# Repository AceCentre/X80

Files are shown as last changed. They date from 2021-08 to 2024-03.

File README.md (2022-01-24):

# X80

X80 is an Arduino-based multi-functional input/output device designed to be an interface between assistive technology inputs such as accessibility switches or specilist sensors and mainstream technology outputs, such as to a mobile phone or Augmentative and Alternative Communication (AAC) device.

An X80 can be preprogrammed and repurposed to perform a different function. It's built around the Adafruit Feather, generally the nrf82540 Express. It's essentially a Feather Wing for Assistive Technology (AT).

There are a couple of smilar projects:

https://github.com/google/mimosa

https://github.com/asterics/FABI

The PCB is still a work in progress but it is designed to have:

* Switch inputs via 3.5mm jack
* switch outputs via 3.5mm jack (simulates a switch press as an input into an Assistive Technology device)
* DB9 connector designed to accomodate devices meeting the TRACE SET Standard often used with accessibility input devices (https://park.org/Guests/Trace/pavilion/setdoc1.htm)
* buzzer
* potentiometer
* on/off switch

There are a few differences between the prototype versions:

## Version 4

The funtionality has been split into two boards:

* X80 Standard (designed for Adafruit ItsyBitsy nrf52840 https://www.adafruit.com/product/4481)
* X80 Power (required for LIPO battery as this board includes the chargin circuit)

### X80 Standard

* Majority surface mount components
* 4 switch inputs (5 with splitter cable on one port)
* 4 switch outputs
* One switch 'pass through' (one switch input will still control on switch output without power)
* buzzer
* setting potentiometer
* header for connecting X80 Power or wiring direct to board)

### X80 Power

* JST connector for LIPO battery
* DB9 connector for connecting external peripherals
* will allow space in enclosure for LIPO battery

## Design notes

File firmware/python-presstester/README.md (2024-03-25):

# Python Press Tester

Designed to Have a switch lead in a Switch jack and repeatedly press it once a second

- Its outputting Switch On/Off But I dont think Im actually pressing the switch output correctly 
- Its not changing the dotstar colour. I dont know why

**NB: ITS CIRCUITPYTHON 9. You NEED THE CIRCUITPYTHON 9 Libraries and firmware for this**

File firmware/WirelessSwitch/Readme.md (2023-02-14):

# Wireless Switch

> ! This is historic - Now see https://github.com/AceCentre/OWS for the most up-to-date  details

## What does this do?

You have a nrf52840 board that sends and a nrf52840 board that receives. We are demonstrating here how to do wireless switches with LOW POWER. 

## How?

Most wireless switches either use Radio (e.g. LoRa) or BLE HID to operate. The problem with BLE HID is that its power hungry and for switch users it cant really sleep. So this technique has a advertisement (advertisement) beacon which starts advertisement on a switch press. Full detail below.. 

On the advertisement (switch sending) board:
- When device sleeps and key button pressed first time, board wakes up. Once the LED lights the board is ready and you can start pairing or transmitting button data.
- When switch is pressed again board starts collecting button data into packages and advertise them.
- It then sends out packages. These data packages are changed every 100ms. Each package has recorded 10 buttons states with interval 10 ms(which in total 100ms).
- After some time of inactivity (5sec default) it will go back to sleep.

On the central (dongle) side:
- It scans BLE devices and for the MAC address device it receives package which has recorded button states over 100ms and then replays these states via USB keyboard (of course you could choose to do this as a joystick button or whatever. That I'm not too bothered about)

## Details

To try this out get two [nrf52840 feather express boards](https://www.adafruit.com/product/4062) from adafruit. Then load up the firmware for each board (its a arduino sketch - you want to first follow the guide [here](https://learn.adafruit.com/introducing-the-adafruit-nrf52840-feather/arduino-bsp-setup)). 

The firmware for the switch sending part is called *advertisement*. You need to add two switches -  one for the actual switch (use a switch jack) and a tactile swich for pairing. 

The firmware for the recievfing part is known as the *central* firmware. There should be defined a LED for indicating pairing. By default it's the red led of a nrf52840 Feather express.

When pairing button is pressed on the advertisement board it will send a specific pairing package and dongle receives this package and MAC address of the board it will listen for. The MAC is saved in flash memory and can be read later on start of dongle code.

Note - to save battery the advertisement board is set to sleep. Pressing the switch will wake it up - all in all this takes around 1 second. 

## Software only technique

So you can use a nrf52840 USB dongle to receive the switch press - or right now you could do it in software alone. See the python directory for this code. 

## Battery life estimates

When pressing key buttton and transmitting data, it consumes around 1000 uA.
In sleep mode it consumes 20 uA.
Good coin cell battery can have around 200 mAh.
So 200mAh/20uA = 10000 hrs in deep sleep mode.
10000hrs > 416 days > a bit more than a year.

But in general cheap batteries will have less capacity.

Consumption can also vary on different boads. My measurements were made with nrf52840 dongle.

## Hardware options

Pretty much any nrf52840 that you can load an arduino sketch onto. 
E.g. 

- [SEEED XIA0 nrf52840](https://shop.pimoroni.com/products/seeed-xiao-ble-nrf52840-supports-arduino-micropython-bluetooth5-0-with-onboard-antenna). Super small - will take a lipo if you solder onto the back batt pins
- [Adafruit nrf52840 express](https://shop.pimoroni.com/products/adafruit-feather-nrf52840-express). A great develeopment board. Has a spare button for you to use as either a pairing button or sending button. 
- [Adafruit itsybitsy nrf52840](https://shop.pimoroni.com/products/adafruit-itsybitsy-nrf52840-express-bluetooth-le). Same as the feather - but smaller and slight less flashy

And for the dongle
- This is nice as its all in one piece. [nrf52840 USB key](https://thepihut.com/products/nrf52840-usb-key-with-tinyuf2-bootloader-bluetooth-low-energy-mdbt50q-rx)

## Roadmap

- [x] Get basic code working
- [x] Add in pairing functionality
- [ ] Get video demo working
- [x] Add in low power features
- [ ] Adapt for x80 
- [x] Write demo code for PC (1/2 done. Can receive switches not send)
- [ ] Create docs page on Ace site
- [ ] Add ability to listen for more than one switch

## Licence

MIT

## Credits 

Will Wade, With a big nod to Prente Romiche/Saltillo and their aeroswitch. Note  - I have no idea if there's does exactly the same as this but a big clue was the fact they called it "Broadcast mode"

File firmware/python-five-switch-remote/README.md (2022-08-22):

# Five Switch Remote

This firmware is a CircuitPython based remote control with five switches.

The centre switch should be plugged into the switch port marked '0' on the X80. The other switches should be plugged into the other jacks and (with a splitter in the port marked '3+').

The four direction arrows will map to a keypress on the coresponding arrow key. You can click and hold for a longer keypress, the press is passed directly through.

The centre key has three options:

- Short press - Will press space
- Medium press - Will press CMD+H
- Long press - Will press EJECT followed by CTRL+TAB

The timings and keys can all be configured in the `user_constants.py` file.

The x80 will pulse with a blue light when it is in 'pairing' mode.

## Setting up circuit python

1. [Download the CircuitPython firmware for the X80 here](https://circuitpython.org/board/itsybitsy_nrf52840_express)
2. [Follow the instructions to flash Circuit Python firmware to the device here](https://learn.adafruit.com/adafruit-itsybitsy-nrf52840-express/circuitpython)
3. Drag the contents of this folder (`python-switcher`) onto the CIRCUITPY device.
4. Done!

To develop the code use [`Code With Mu`](https://codewith.mu/). It will automatically connect to the device if its plugged in. You can set it up with VSCode but honestly its not worth the hassle

## Configuration

All of the X80 configuration is found in `x80_constants.py`. This creates a bunch of constants specific to the x80 like what switches are connected to what pins and what pull mode the switches are in. These shouldn't need to be changed between users.

The `user_constants.py` is where we can tweak the behaviour of the switcher. Change which ports we want to enable and the colors of the LED etc.=xnk

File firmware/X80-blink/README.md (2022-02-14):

# X80-blink
Demonstrate blink detection using the X80 interface device.

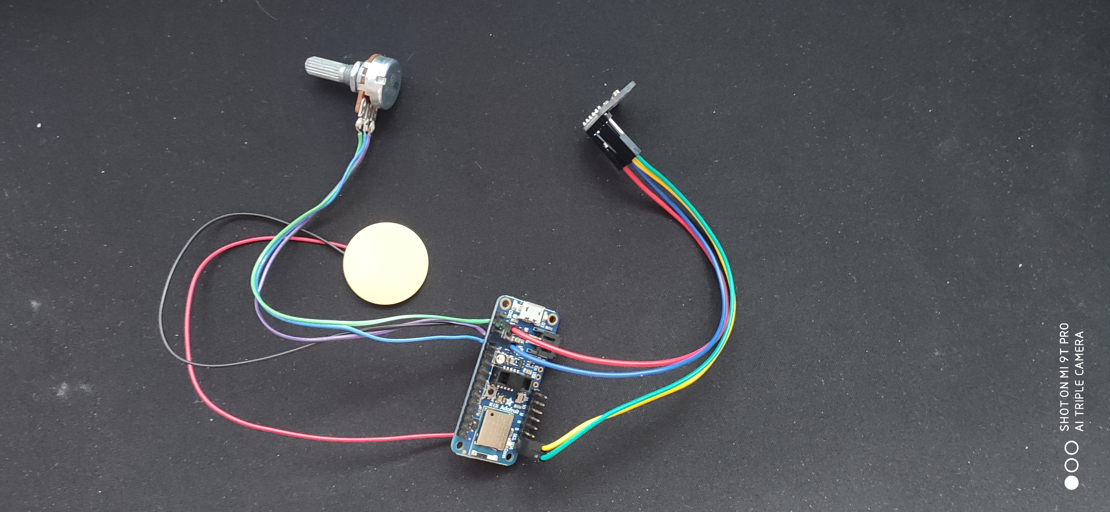
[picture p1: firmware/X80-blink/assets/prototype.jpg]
Breadboard prototype


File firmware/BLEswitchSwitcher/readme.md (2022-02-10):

What does this do?

- Use one or two switches
- Pair it with your device
- With switch 3 - it will change the MAC address of the device
- With switch 4 - It will change the name of the device

This theoretically means you can use one switch for different apps on Android - or on iOS swap the mac address

** WARNING: NOT TESTED **

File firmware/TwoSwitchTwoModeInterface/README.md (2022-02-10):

# TwoSwitchTwoModeInterface
 Simple Arduino/Adafruit nrf52840 express feather sketch demonstrating how to change MAC address

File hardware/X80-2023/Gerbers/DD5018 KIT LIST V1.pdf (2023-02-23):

Assembly Ref | A06-02 | Job No. | C2698 | Kit Prep 1 hour | Assembly time ?? mins per board
Build Qty | 1 | UNIT WEIGHT
Mj Ref | Qty per board | Kit Qty | Kitted | Board Ref | Description | Suppler | Ref
A06-01 | 1 | 1 | 1 | A1 | ADAFRUIT FEATHER BASIC ATSAMD21 CORTEX M0 | MOUSER | 485-2772
A06-02 | 1 | 1 | 1 | BUZ1 | AUDIO MAGNETIC XDCR 3-5V SMD | Digikey | 102-3736-1-ND
A06-03 | 10 | 10 | 20 | C1, C2, C3, C4, C5, C6, C7, C8, C10, C11 | CAP CER 10NF 50V X7R 0603 | Farnell | 2346966
A06-04 | 2 | 2 | 5 | D1, D2 | DIODE GEN PURP 100V 300MA SOD123 | Farnell | 3127171
A06-05 | 0 | 0 | 9 | J1, J2, J4, J6, J7, J8, J9, J10, J11 | 3.5 mm PCB Mount Stereo Jack Socket, 4Pole 1A | Farnell | 2677783
A06-06 | 1 | 1 | 1 | J5 | 4 Pole Side Entry Shrouded Header 2.00mm | Rapid | 22-5204
A06-07 | 1 | 1 | 1 | K1 | DPDT telecom PCB relay, 2A 3Vdc coil, EA | Farnell | 1326155
A06-08 | 2 | 2 | 5 | Q1, Q2 | TRANS NPN 40V 0.6A SMD SOT23-3 | Farnell | 1773626
A06-09 | 1 | 1 | 5 | Q3 | BIASED 50V 100mA | Farnell | 3368898
A06-10 | 1 | 1 | 10 | R1 | RES SMD 3.3K OHM 1% 1/10W 0603 | Farnell | 9238549
A06-11 | 2 | 2 | 10 | R2, R7 | RES 1K OHM 0.1% 1/10W 0603 | Farnell | 2502396
A06-12 | 1 | 1 | 10 | R3 | RES SMD 100K OHM 1% 1/10W 0603 | Farnell | 9238727
A06-13 | 1 | 1 | 5 | R4 | 10kΩ, Trimmer Potentiometer 0.2W Top Bourns, 3306P | Farnell | 108239
A06-14 | 2 | 2 | 10 | R5, R6 | RES SMD 4.7K OHM 5% 1/10W 0603 | Farnell | 9233466
A06-15 | 11 | 11 | 20 | R8, R9, R10, R11, R12, R18, R19, R20, R21, R22, R23 | RES SMD 100 OHM 1% 1/10W 0603 | Farnell | 9238360
A06-16 | 4 | 4 | 10 | R13, R14, R15, R16 | RES SMD 390 OHM 5% 1/10W 0603 | Farnell | 9233326
A06-17 | 1 | 1 | 10 | R17 | RES SMD 22K OHM 5% 1/10W 0603 | Farnell | 9233547
A06-18 | 1 | 1 | 10 | SW1 | PUSHBUTTON SMD | Farnell | 9471898
A06-19 | 4 | 4 | 4 | U1, U2, U3, U4 | 1 Form A Solid-State Relay (NO) | Farnell | 1470184

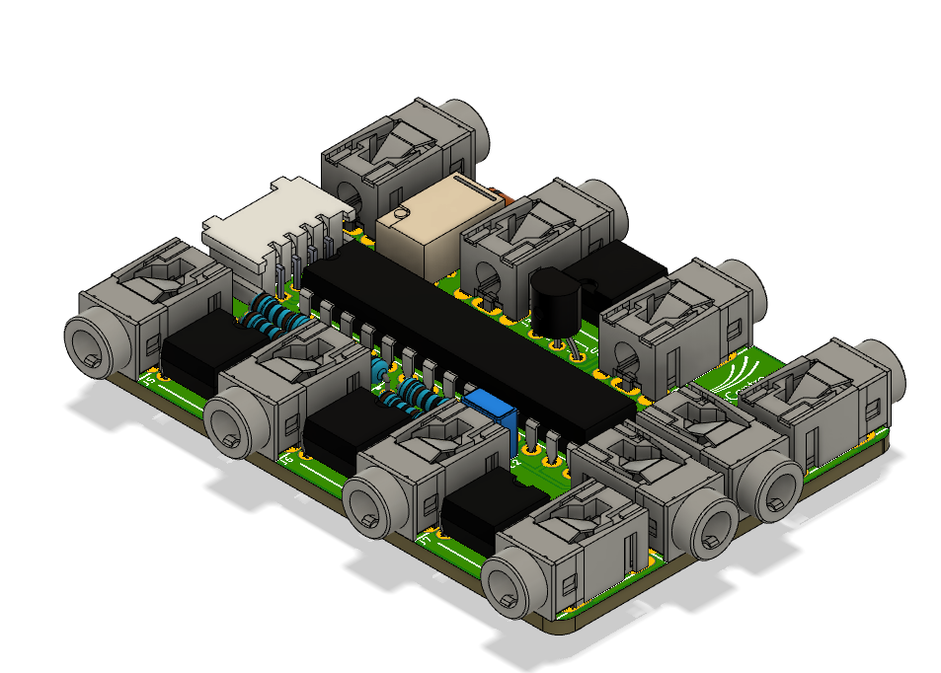
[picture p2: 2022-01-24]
hardware/X80 Wio Terminal/X80 Wio Terminal.png

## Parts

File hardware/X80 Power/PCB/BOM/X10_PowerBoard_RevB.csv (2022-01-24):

Qty | Value | Device | Package | Parts | Description | DESCRIPTION | MF | MFR | MFR_NUM | MPN | OC_FARNELL | POPULARITY | SPICEPREFIX | VALUE | VENDOR | VENDOR_NUM
3 |  | 1,6/0,8 | 1,6/0,8 | PAD1, PAD2, PAD3 | THROUGH-HOLE PAD |  |  |  |  |  |  | 15
1 |  | LEDSML0603 | SML0603 | LED1 | LED |  |  |  |  |  |  | 17
1 | 0.1uF | C-EUC0603 | C0603 | C1 | CAPACITOR, European symbol |  |  |  |  |  |  | 73 | C
1 | 100k | R-100K-1%-0603 | RESC1608X60 | R10 | SMD Resistor | RES SMD 100K OHM 1% 1/10W 0603 |  | Yageo | RC0603FR-07100KL |  |  |  |  | 100k | Digi-Key | 311-100KHRCT-ND
1 | 239-5849 | DB9_MALE-SLOTS | DB9_PLUG_SLOT | J1 | D-SUB Connector - Right Angle | D-sub Connector - 2.77mm Pitch |  | RS Pro | 239-5849 |  |  |  |  | 239-5849 | RS-Online | 239-5849
2 | 4.7uF | C-4.7UF-10V-X5R-0603 | CAPC1608X85 | C11, C14 |  | CAP CER 4.7UF 10V X5R 0603 |  | Samsung Electro-Mechanics | CL10A475KP8NNNC |  | unknown |  |  | 4.7uF | Digi-Key | 1276-1044-1-ND
1 | 470R | R-BACKUP-470R-1%-0603 | RESC1608X60 | R1 | SMD Resistor | RES SMD 470 OHM 1% 1/10W 0603 |  | Yageo | RC0603FR-07470RL |  |  |  |  | 470R | Digi-Key | 311-470HRCT-ND
1 | 5.1k | R-5.1K-1%-0603 | RESC1608X60 | R8 | SMD Resistor | RES SMD 5.1K OHM 1% 1/10W 0603 |  | Yageo | RC0603FR-075K1L |  |  |  |  | 5.1k | Digi-Key | 311-5.10KHRCT-ND
1 | CONN2_05-HEADER | CONN2_05-HEADER | 2X5_HEADER | J3
1 | CONN_02-S2B-PH | CONN_02-S2B-PH | S2B-PH-RA | J4
1 | DMP2035U-7 | P-MOSFET-DMP2035U-7-SOT323 | SOT95P230X110-3N | Q1 | P MOSFET | MOSFET P-CH 20V 3.6A SOT-23 |  | Diodes Incorporated | DMP2035U-7 |  |  |  |  | DMP2035U-7 | Digi-Key | DMP2035U-7DICT-ND
1 | FUSE0603 | FUSE0603 | FUSC1607X75N | F1
1 | LOGO-10MM | LOGO-10MM | LOGO_10MM | U$2
1 | MBR120VLSFT3G | DIODE-SCHOTTKY-20V-1ASOD-123FL | SODFL3616X98N | D3 | Schottky Diode | Semiconductor DIODE SCHOTTKY 20V 1A SOD123FL |  | On Semiconductor | MBR120VLSFT3G |  |  |  |  | MBR120VLSFT3G | Digi-Key | MBR120VLSFT3GOSCT-ND
1 | MCP23008/P | MCP23008/P | DIL18 | U2 | MCP23008
1 | MCP73831 | MCP73831 | SOT23-5P95_270X145L35X35N | U3 | MCP73831 - Single-Cell, Fully Integrated Li-Ion,Li-Polymer Charge Management Controllers | Single-Cell, Fully Integrated Li-Ion,Li-Polymer Charge Management Controllers |  | Microchip | MCP73831T-2ACI/OT |  | unknown |  |  | MCP73831 | DigiKey | MCP73831T-2ACI/OTCT-ND
1 | SDPT | SLIDE_SWITCH | OS102011MA1QN1 | S2 | Switch Slide Right Angle SPDT 0.1A 12VDC Through Hole Slide Switch SPDT On-On 0.1 A@ 12 V dc Slide | Switch Slide Right Angle SPDT 0.1A 12VDC Through Hole Slide Switch SPDT On-On 0.1 A@ 12 V dc Slide |  | C & K COMPONENTS | OS102011MA1QN1 |  |  |  |  | SDPT | RS-ONLINE
1 | X10_PWR_PCB-X10_PWR_PCB | X10_PWR_PCB-X10_PWR_PCB | X10_POWER_PCB | PCB1

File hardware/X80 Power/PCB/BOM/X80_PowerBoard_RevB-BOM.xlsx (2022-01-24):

Item # | Ref Des | Qty | Description | Manufacturer | Manufacturer part-name | Value | Package
1 | C1 | 1 | CAP CER 0.1UF 25V X7R 0603 | KEMET | C0603C104K3RAC7411 | 0.1uF | 0603
2 | C2, C3 | 2 | CAP CER 4.7UF 10V X5R 0603 | Samsung Electro-Mechanics | CL10A475KP8NNNC | 4.7uF | 0603
3 | D1 | 1 | Semiconductor DIODE SCHOTTKY 20V 1A SOD123FL | On Semiconductor | MBR120VLSFT3G | MBR120VLSFT3G | SOD-123FL
4 | F1 | 1 | PTC RESET FUSE 6V 500MA 0603 | Bourns | MF-FSMF050X-2 | FUSE0603 | 0603
5 | IC1 | 1 | IC I/O EXPANDER I2C 8B 18DIP | Microchip Technology | MCP23008-E/P | MCP23008/P | DIP-18
6 | J1 | 1 | D-sub Connector - 2.77mm Pitch | RS Pro | 239-5849 | 239-5849 | THT
7 | J2 | 1 | CONN HEADER R/A 2POS 2MM | JST Sales America Inc. | S2B-PH-K-S(LF)(SN) | CONN_02-S2B-PH | THT
10 | J3 | 1 | CONN HEADER VERT 10POS 2.54MM | Adam Tech | PH2-10-UA | CONN2_05-HEADER | THT
11 | LED1 | 1 | LED RED DIFFUSED 0603 SMD | Würth Elektronik | 150060SS55040 | RED | 0603
12 | Q1 | 1 | MOSFET P-CH 20V 3.6A SOT-23 | Diodes Incorporated | DMP2035U-7 | DMP2035U-7 | 0603
13 | R1 | 1 | RES SMD 470 OHM 1% 1/10W 0603 | Yageo | RC0603FR-07470RL | 470R | 0603
14 | R2 | 1 | RES SMD 5.1K OHM 1% 1/10W 0603 | Yageo | RC0603FR-075K1L | 5.1k | 0603
15 | R3 | 1 | RES SMD 100K OHM 1% 1/10W 0603 | Yageo | RC0603FR-07100KL | 100k | THT
16 | S1 | 1 | Switch Slide Right Angle SPDT 0.1A 12VDC Through Hole Slide Switch SPDT On-On 0.1 A@ 12 V dc Slide | C & K COMPONENTS | OS102011MA1QN1 | SDPT | 0603
17 | U1 | 1 | Single-Cell, Fully Integrated Li-Ion,Li-Polymer Charge Management Controllers | Microchip | MCP73831T-2ACI/OT | MCP73831 | 0603

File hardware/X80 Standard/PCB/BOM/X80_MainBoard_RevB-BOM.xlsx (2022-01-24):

Item # | Ref Des | Qty | Description | Manufacturer | Manufacturer part-name | Value | Package
1 | BUZ1 | 1 | AUDIO MAGNETIC XDCR 3-5V SMD | CUI Devices | CMT-8530S-SMT-TR | CMT-8530S-SMT | SMD-4
2 | C1, C2, C3, C4, C5 | 5 | CAP CER 10NF 50V X7R 0603 | Samsung | CL10B103KB8WPJC | 10nF | THT
3 | D1, D2 | 2 | DIODE GEN PURP 100V 300MA SOD123 | Diodes Incorporated | 1N4148WQ-7-F | 1N4148 | SOD-123
4 | J1, J2, J3, J4, J8, J9, J10, J11 | 8 | 3.5 mm PCB Mount Stereo Jack Socket, 4Pole 1A | Lumberg | 1503 19 | Stereo Jack | THT
5 | J5 | 1 | CONN HDR 10POS(2x5) 2.54MM GOLD FEMALE THT | Würth Elektronik | 61301021821 | 2x5 | THT
6 | J6, J7 | 2 | CONN HEADER VERT 14POS 2.54MM | Adam Tech | PH1-14-UA | 1x14 | THT
7 | K1 | 1 | DPDT telecom PCB relay, 2A 3Vdc coil, EA | TE Connectivity | 1462037-4 | IM01TS | THT
10 | Q1, Q2 | 2 | TRANS NPN 40V 0.6A SMD SOT23-3 | Diodes Incorporated | MMBT2222A-7-F | MMBT2222A-7-F | SOT-23
11 | R1 | 1 | RES SMD 3.3K OHM 1% 1/10W 0603 | Yageo | RC0603FR-073K3L | 3.3k | 0603
12 | R12, R13, R14, R15, R16 | 5 | RES SMD 100 OHM 1% 1/10W 0603 | Yageo | RC0603FR-07100RL | 100R | 0603
13 | R2 | 1 | RES SMD 100K OHM 1% 1/10W 0603 | Yageo | RC0603FR-07100KL | 100k | 0603
14 | R3, R4 | 2 | RES 1K OHM 0.1% 1/10W 0603 | Yageo | RC0603FR-071KL | 1k | 0603
15 | R5 | 1 | 10kΩ, Trimmer Potentiometer 0.2W Top Bourns, 3306P | Bourns | 3306P-1-103 | 10k | THT
16 | R6, R7 | 2 | RES SMD 4.7K OHM 5% 1/10W 0603 | Yageo | RC0603JR-074K7L | 4.7k | 0603
17 | R8, R9, R10, R11 | 4 | RES SMD 390 OHM 5% 1/10W 0603 | Yageo | RC0603JR-07390RL | 390R | 0603
18 | SW1 | 1 | White Tactile Switch, Single Pole Single Throw (SPST) | Wurth Elektronik | 431256031716 | 431256031716 | THT
19 | U1, U2, U3, U4 | 4 | 1 Form A Solid-State Relay (NO) | Vishay | LH1500AT | LH1500AT | PDIP-6

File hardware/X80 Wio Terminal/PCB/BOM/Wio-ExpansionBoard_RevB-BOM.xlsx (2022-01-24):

Item # | Ref Des | Qty | Description | Manufacturer | Manufacturer part-name | Value | Package | RS-ONLINE_NUM
1 | C1, C2, C3, C4, C5, C6, C7, C8 | 8 | 10nF Multilayer Ceramic Capacitor MLCC 50V dc ±10% | KEMET | C315C103K5R5TA | 10nF | THT | 538-1196
2 | C9 | 1 | Murata 100nF Multilayer Ceramic Capacitor MLCC 50V dc ±15% | Murata | RCER71H104K0K1H03B | 100nF | THT | 841-0749
3 | D1 | 1 | Switching Diode, 400mA 100V, 2-Pin DO-35 1N4148TR | On Semiconductor | 1N4148TR | 1N4148 | THT | 671-5477
4 | J1, J2, J3, J4, J5, J6, J7, J8, J9, J10 | 10 | 3.5 mm PCB Mount Stereo Jack Socket, 4Pole 1A | Lumberg | 1503 19 | Stereo Jack | THT | 124-8885
5 | J11 | 1 | Groove Female Header - DIP-4P-2,0mm-90D |  |  |  | THT | https://www.seeedstudio.com/Grove-Universal-4-pin-connector-90-10-PCs.html
6 | K1 | 1 | DPDT telecom PCB relay, 2A 3Vdc coil, EA | TE Connectivity | 1462037-4 | IM01TS | THT | 909-7996
7 | Q1 | 1 | NPN General-Purpose Amplifier | On Semiconductor | PN2222ABU | PN2222A | TO-92 | 739-0555
8 | R1 | 1 | RS PRO 1kΩ Carbon Film Resistor 0.25W ±5% | RS PRO | 707-7666 | 1k | THT | 707-7666
9 | R2, R3, R4, R5 | 4 | RS PRO 390Ω Carbon Film Resistor 0.25W ±5% | RS PRO | 707-7634 | 390R | THT | 707-7634
10 | U1, U2, U3, U4 | 4 | 1 Form A Solid-State Relay (NO) | Vishay | LH1500AT | LH1500AT | PDIP-6 | 180-8794
11 | U5 | 1 | IC I/O EXPANDER I2C 16-Bit 28SDIP | Microchip | MCP23017-E/SP | MCP23017 | PDIP28 | 144-5723

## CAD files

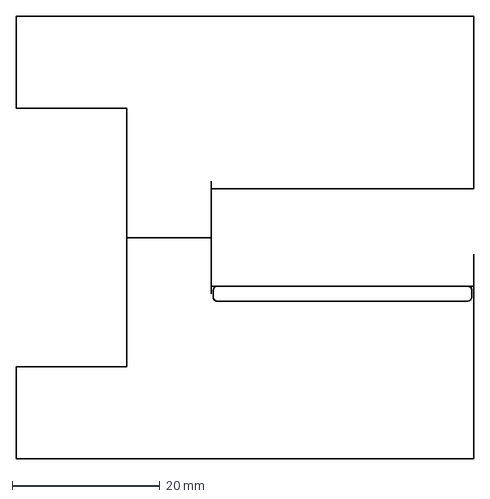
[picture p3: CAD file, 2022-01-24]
hardware/X80 Standard/PCB/Mechanical/MainBoard.dxf
62.0 x 60.0 mm

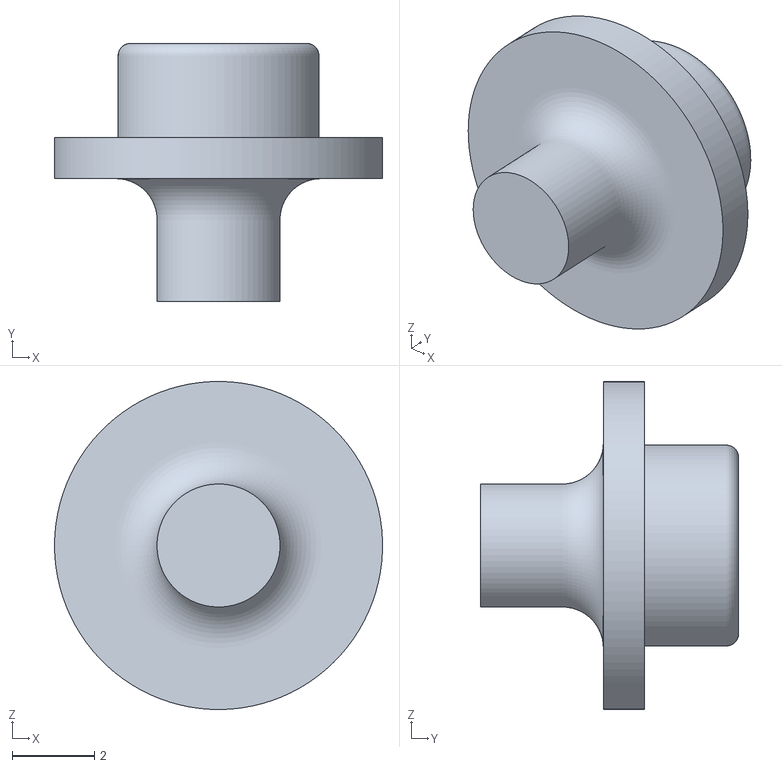
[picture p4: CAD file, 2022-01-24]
hardware/Parts/Lens/630-005-A X80 LED Lens.stl
8.00 x 6.30 x 8.00

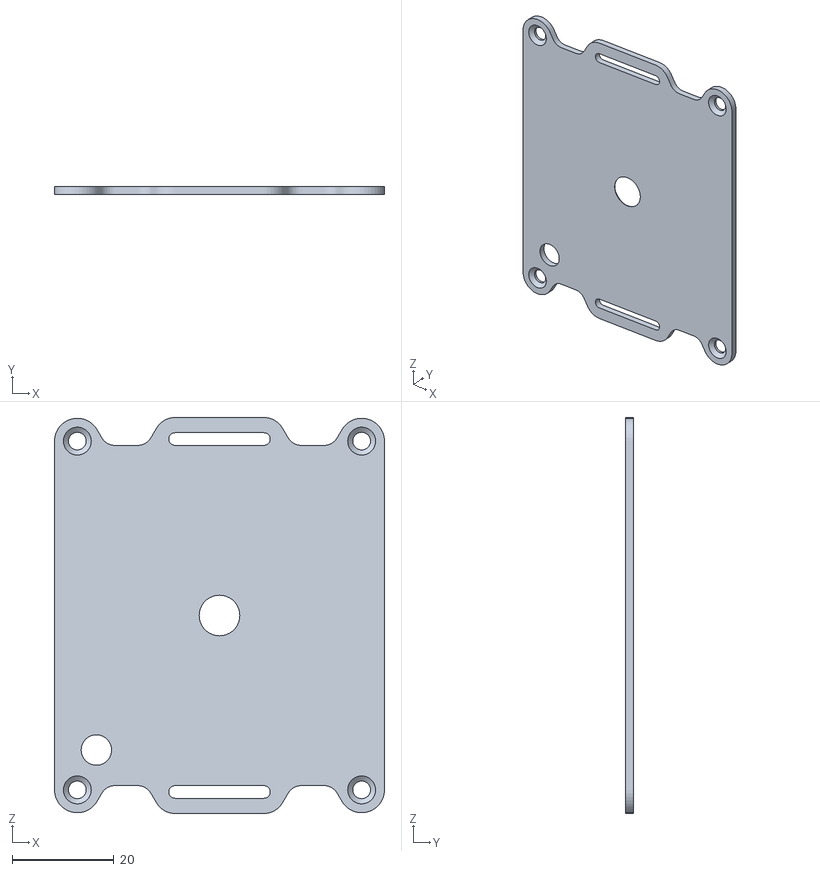
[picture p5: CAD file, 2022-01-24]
hardware/Parts/Mounting Plate/630-006-B X80 Mounting Plate.stl
65.0 x 1.60 x 78.0

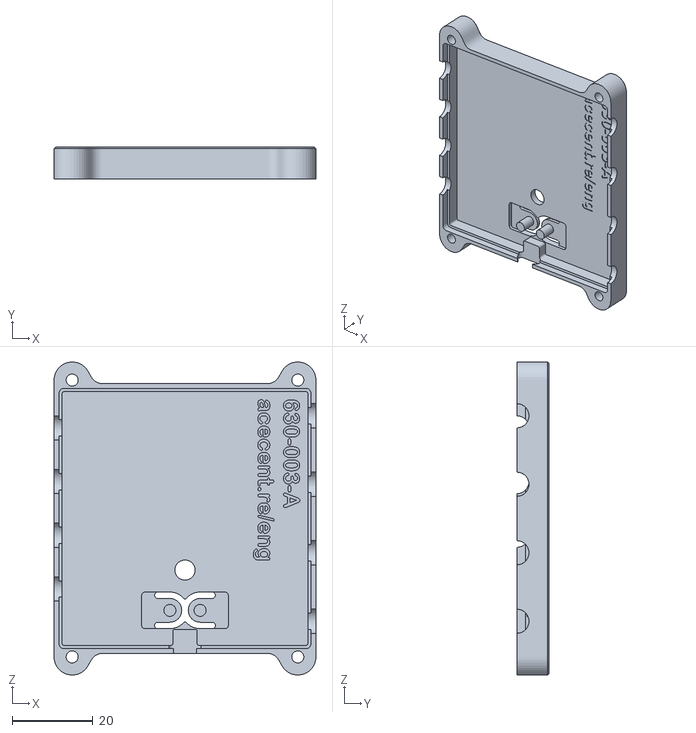
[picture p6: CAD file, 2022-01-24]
hardware/X80 Standard/Enclosure Basic/630-003-A X80 Enclosure Lid Basic.stl
65.0 x 8.00 x 77.7

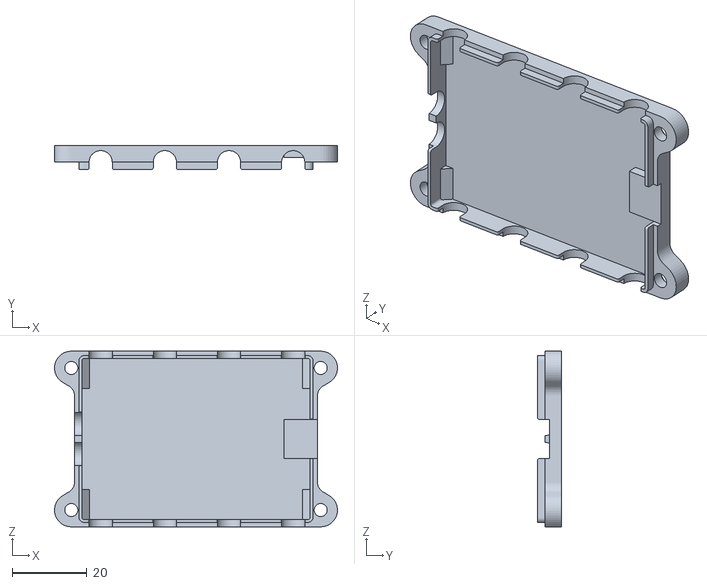
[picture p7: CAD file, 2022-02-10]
hardware/X80 Wio Terminal/Enclosure/630-014 X80 Enclosure Wio Terminal Lid.stl
75.7 x 6.50 x 47.0

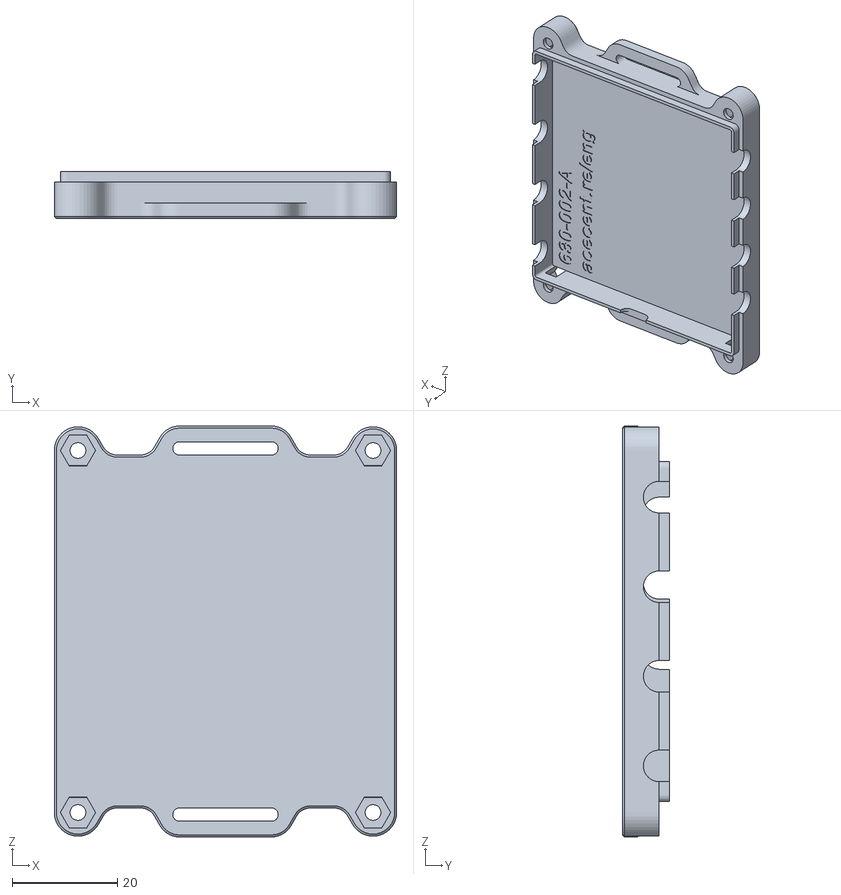
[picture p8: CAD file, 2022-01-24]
hardware/X80 Standard/Enclosure Basic/630-002-A X80 Enclosure Base Basic.stl
65.0 x 9.00 x 78.0

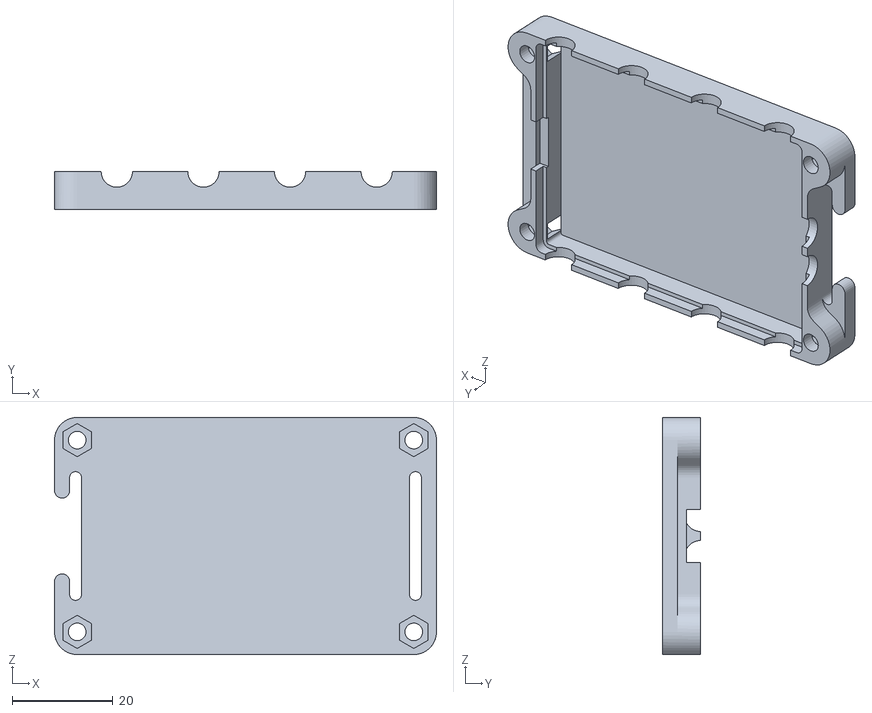
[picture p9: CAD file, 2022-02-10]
hardware/X80 Wio Terminal/Enclosure/630-014 X80 Enclosure Wio Terminal Base.stl
75.7 x 7.50 x 47.0

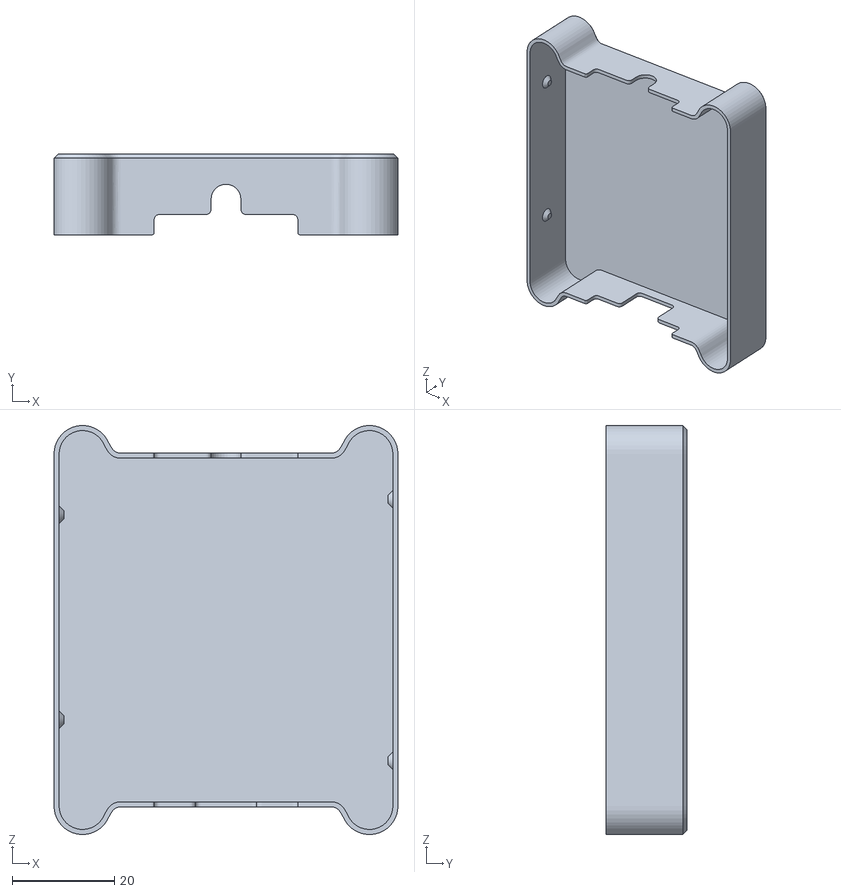
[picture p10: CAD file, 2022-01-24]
hardware/X80 Standard/Enclosure with Grommet/630-011-A X80 Grommet Splash Cover.stl
67.1 x 15.8 x 79.8

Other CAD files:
hardware/X80 Standard/Enclosure with Grommet/630-010-B X80 Enclosure Grommet Lid.stl
hardware/X80 Standard/Enclosure with Grommet/630-009-A X80 Enclosure Grommet Base.stl
hardware/Parts/Mounting Plate/630-006-B X80 Mounting Plate.dxf

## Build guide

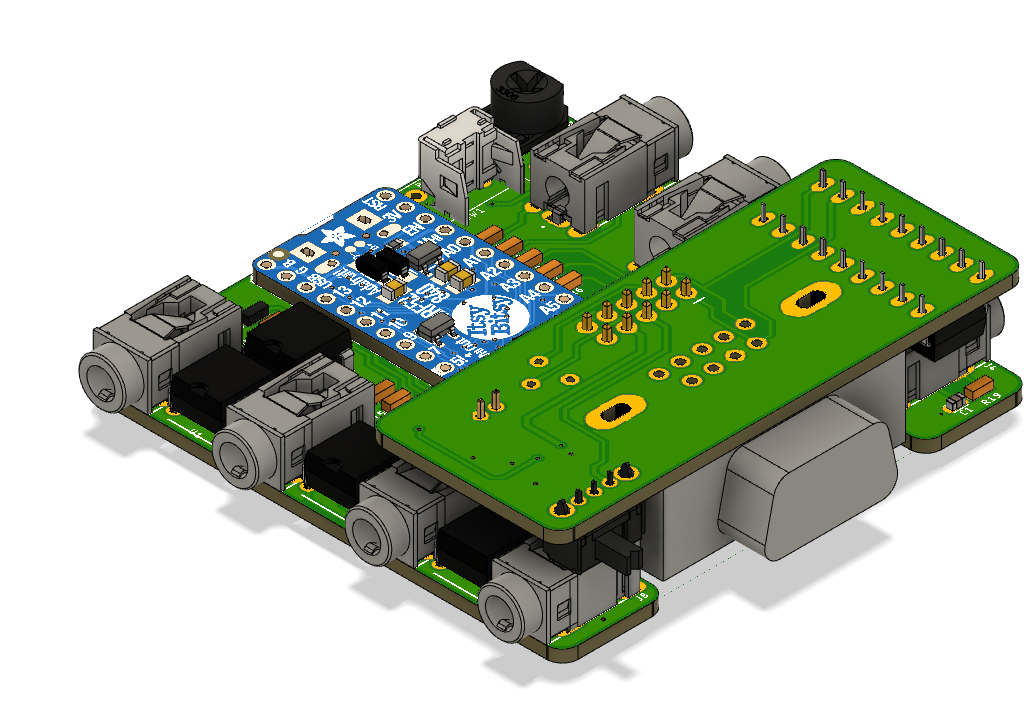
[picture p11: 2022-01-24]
hardware/X80 Power/X80 Power Assembly.png

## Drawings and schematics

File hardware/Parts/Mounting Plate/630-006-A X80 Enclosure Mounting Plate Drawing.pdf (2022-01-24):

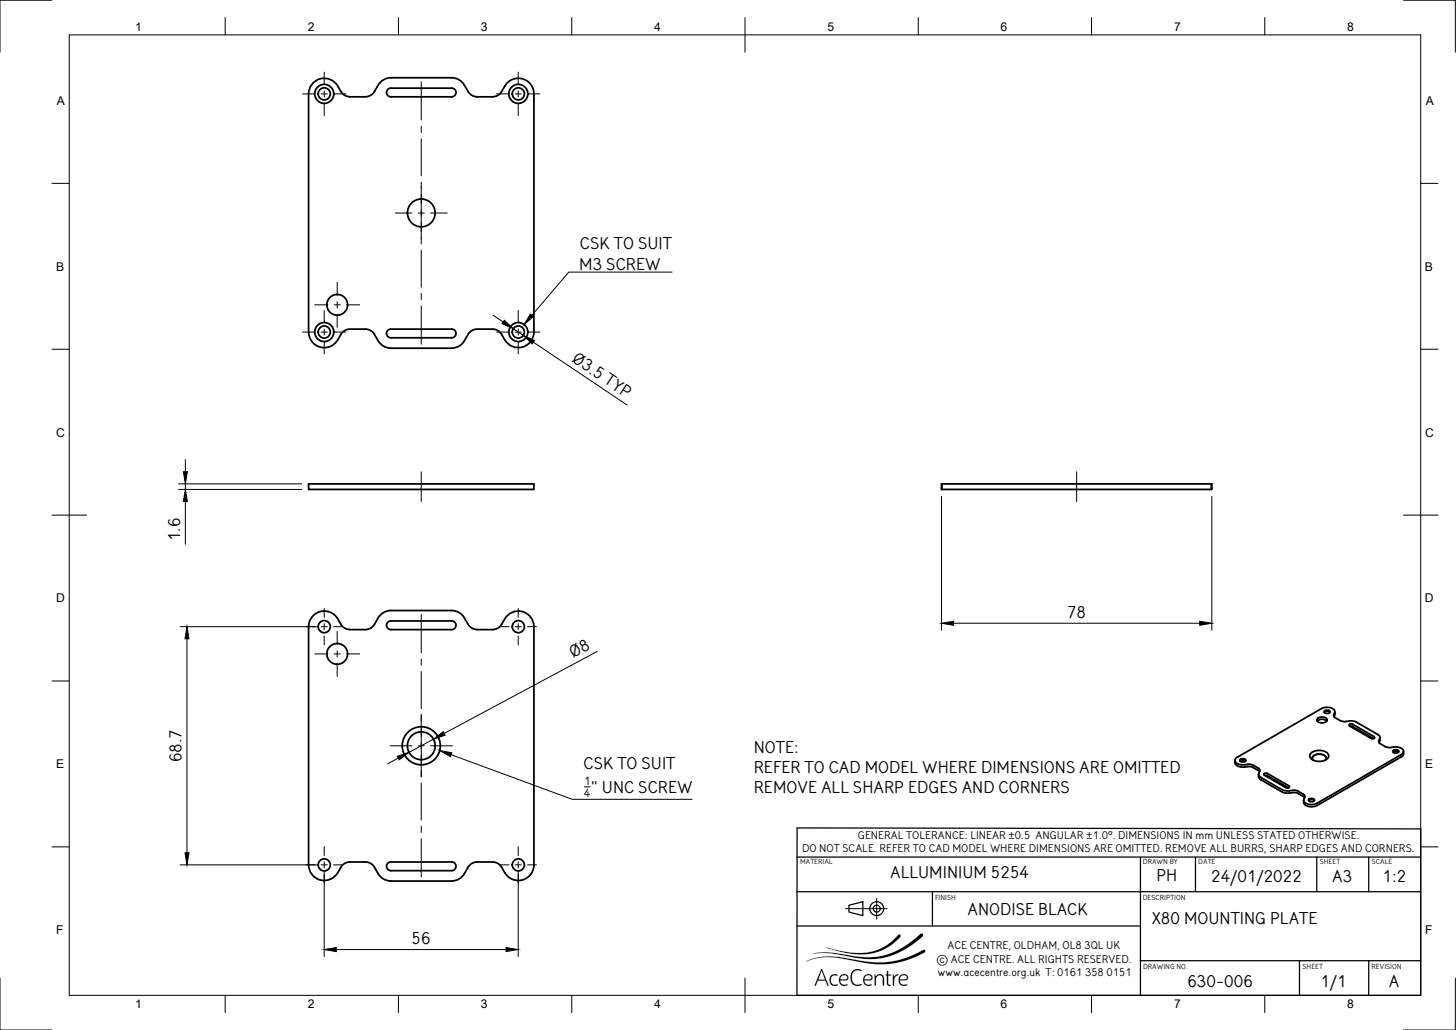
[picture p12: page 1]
DRAWING NO.; X80 MOUNTING PLATE 1.6; Ø3.5 TYP

CSK TO SUIT
M3 SCREW

NOTE:
REFER TO CAD MODEL WHERE DIMENSIONS ARE OMITTED
REMOVE ALL SHARP EDGES AND CORNERS

4" UNC SCREW

GENERAL TOLERANCE: LINEAR ±0.5 ANGULAR ±1.0°. DIMENSIONS IN mm UNLESS STATED OTHERWISE.

DO NOT SCALE. REFER TO CAD MODEL WHERE DIMENSIONS ARE OMITTED. REMOVE ALL BURRS, SHARP EDGES AND CORNERS. DESCRIPTION MATERIAL FINISH ALLUMINIUM 5254 | DRAWN BY PH | DATE 24/01/2022 | SHEET A3 | SCALE 1:2

ANODISE BLACK | SHEET REVISION ACE CENTRE, OLDHAM, OL8 3QL UK

© ACE CENTRE. ALL RIGHTS RESERVED.
www.acecentre.org.uk T: 0161 358 0151

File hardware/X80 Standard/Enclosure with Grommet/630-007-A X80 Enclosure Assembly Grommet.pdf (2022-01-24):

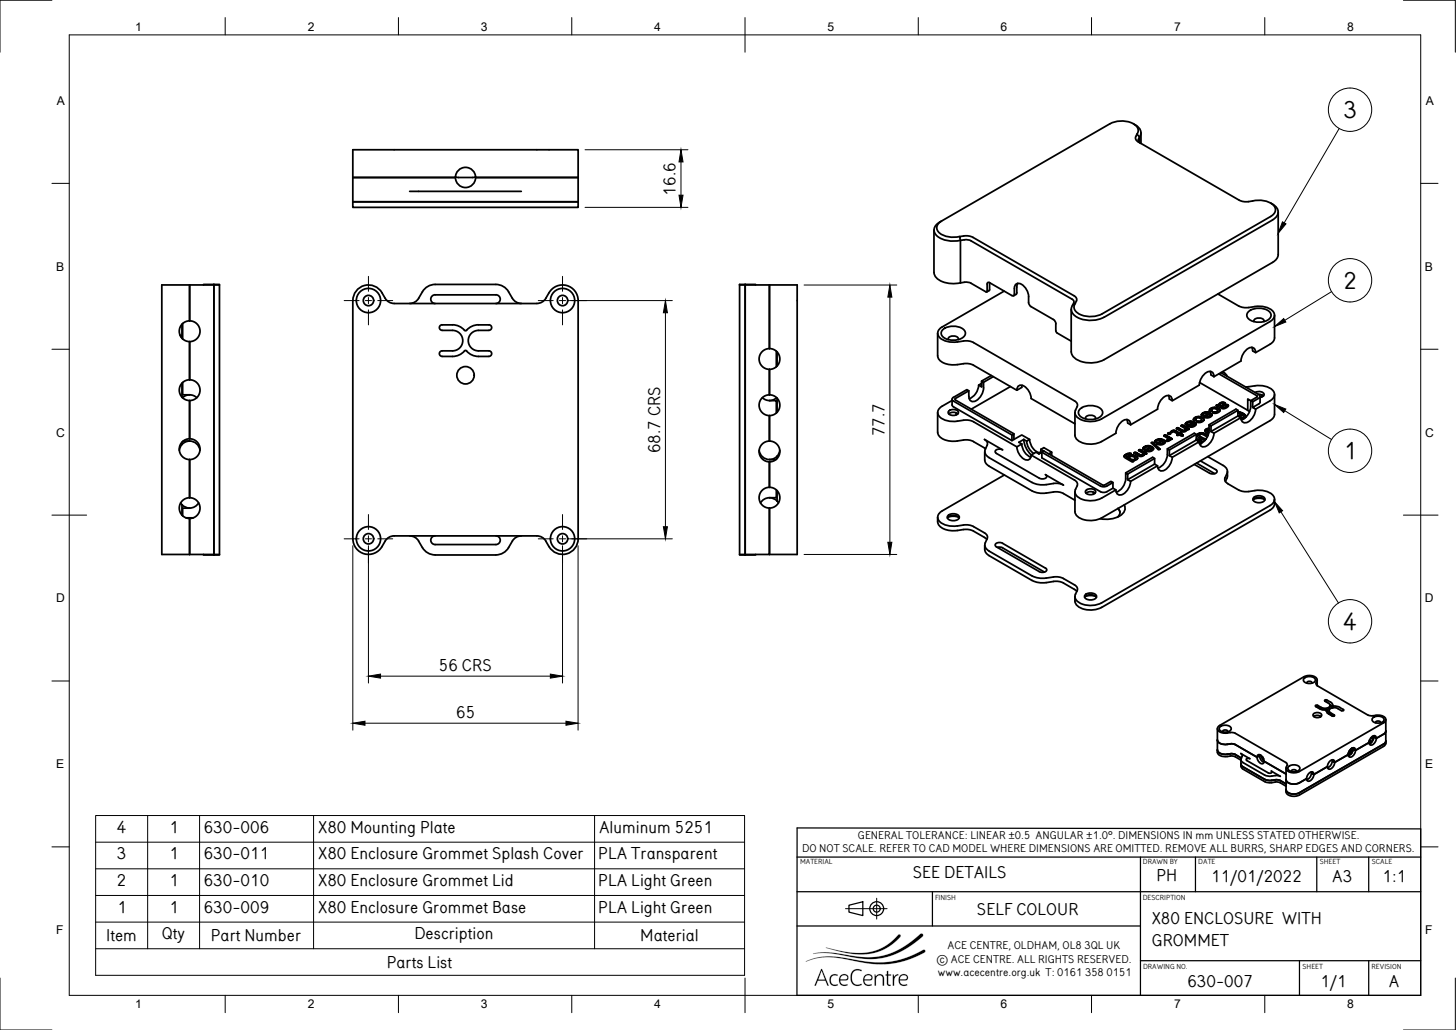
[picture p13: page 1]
DRAWING NO.; X80 ENCLOSURE WITH 16.6; 56 CRS; 68.7 CRS; Parts List

4 | 1 | 630-006 | X80 Mounting Plate | Aluminum 5251
3 | 1 | 630-011 | X80 Enclosure Grommet Splash Cover | PLA Transparent
2 | 1 | 630-010 | X80 Enclosure Grommet Lid | PLA Light Green
1 | 1 | 630-009 | X80 Enclosure Grommet Base | PLA Light Green
Item | Qty | Part Number | Description | Material

GENERAL TOLERANCE: LINEAR ±0.5 ANGULAR ±1.0°. DIMENSIONS IN mm UNLESS STATED OTHERWISE.

DO NOT SCALE. REFER TO CAD MODEL WHERE DIMENSIONS ARE OMITTED. REMOVE ALL BURRS, SHARP EDGES AND CORNERS. DESCRIPTION MATERIAL FINISH SEE DETAILS | DRAWN BY PH | DATE 11/01/2022 | SHEET A3 | SCALE 1:1

SELF COLOUR | GROMMET SHEET REVISION ACE CENTRE, OLDHAM, OL8 3QL UK

© ACE CENTRE. ALL RIGHTS RESERVED.
www.acecentre.org.uk T: 0161 358 0151

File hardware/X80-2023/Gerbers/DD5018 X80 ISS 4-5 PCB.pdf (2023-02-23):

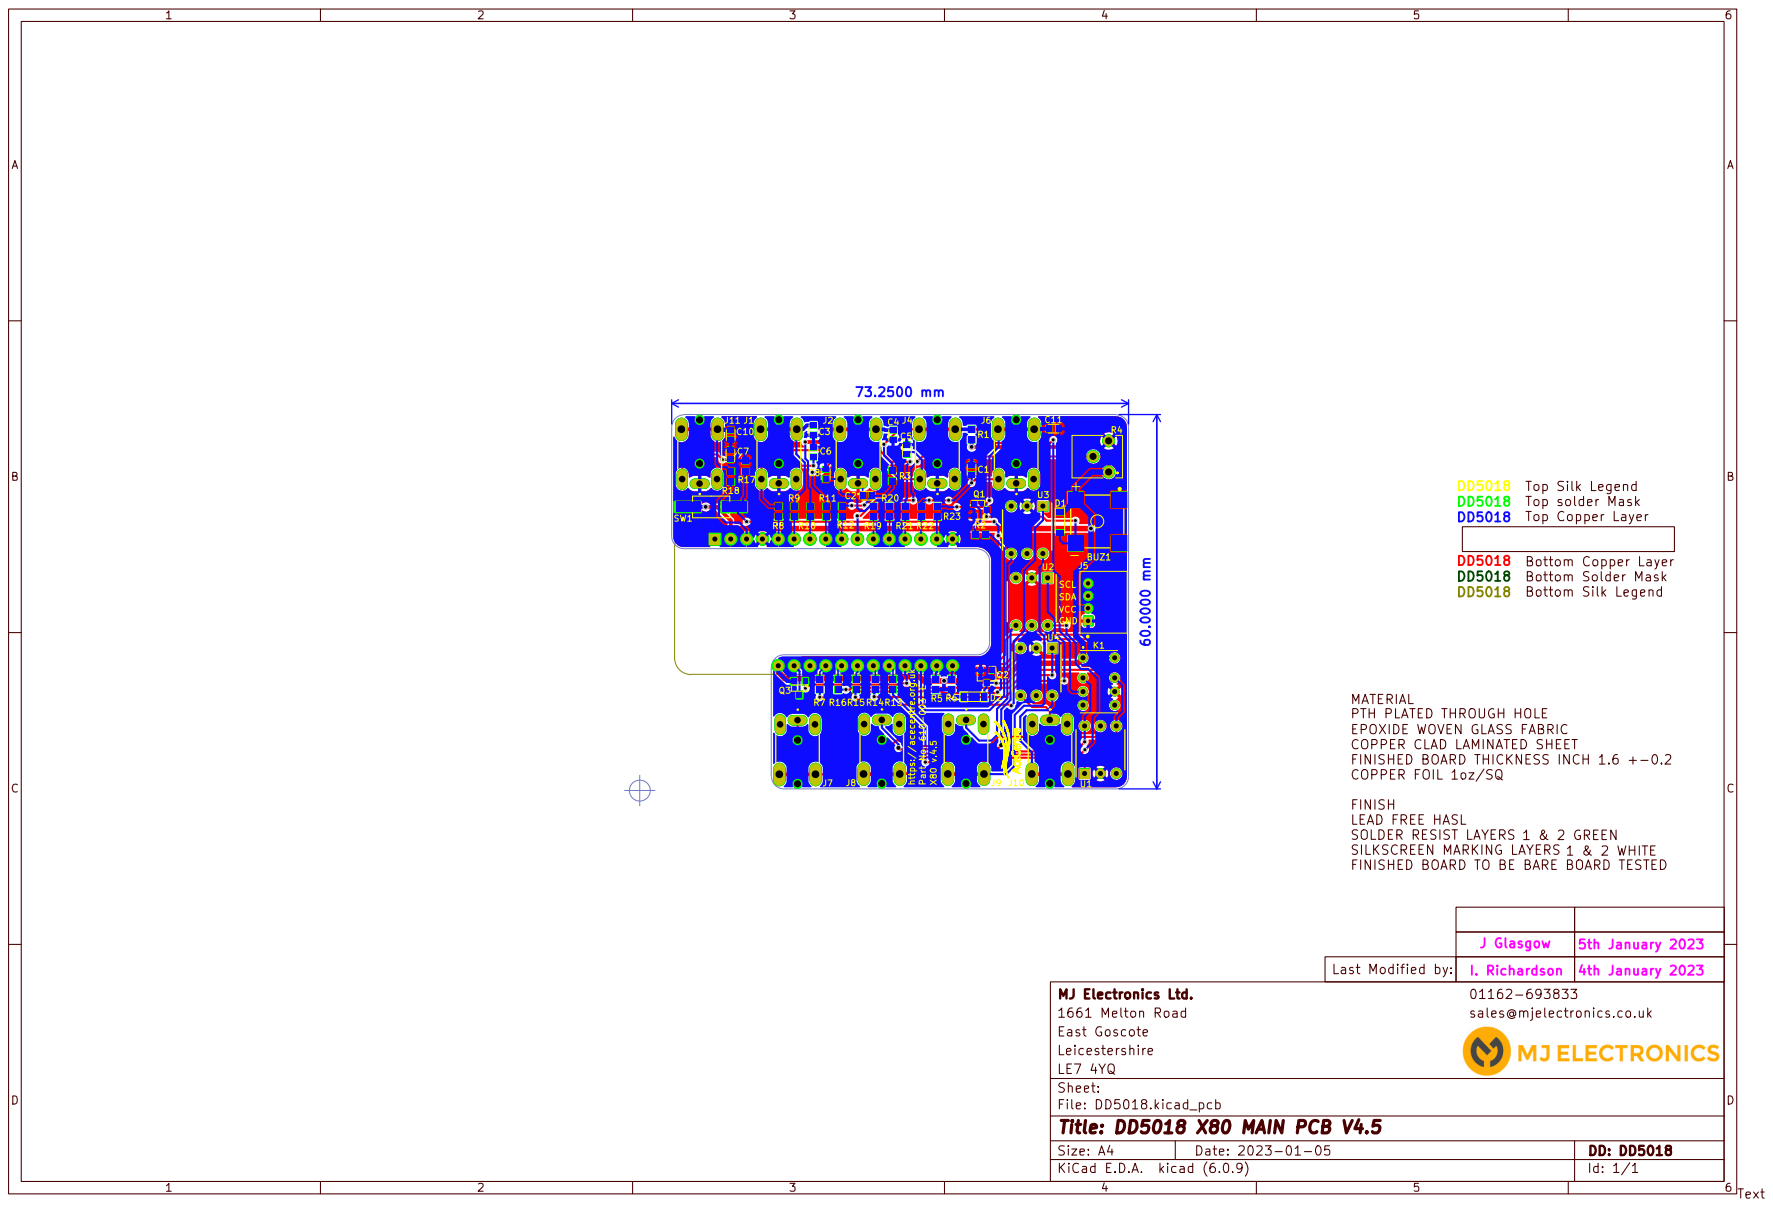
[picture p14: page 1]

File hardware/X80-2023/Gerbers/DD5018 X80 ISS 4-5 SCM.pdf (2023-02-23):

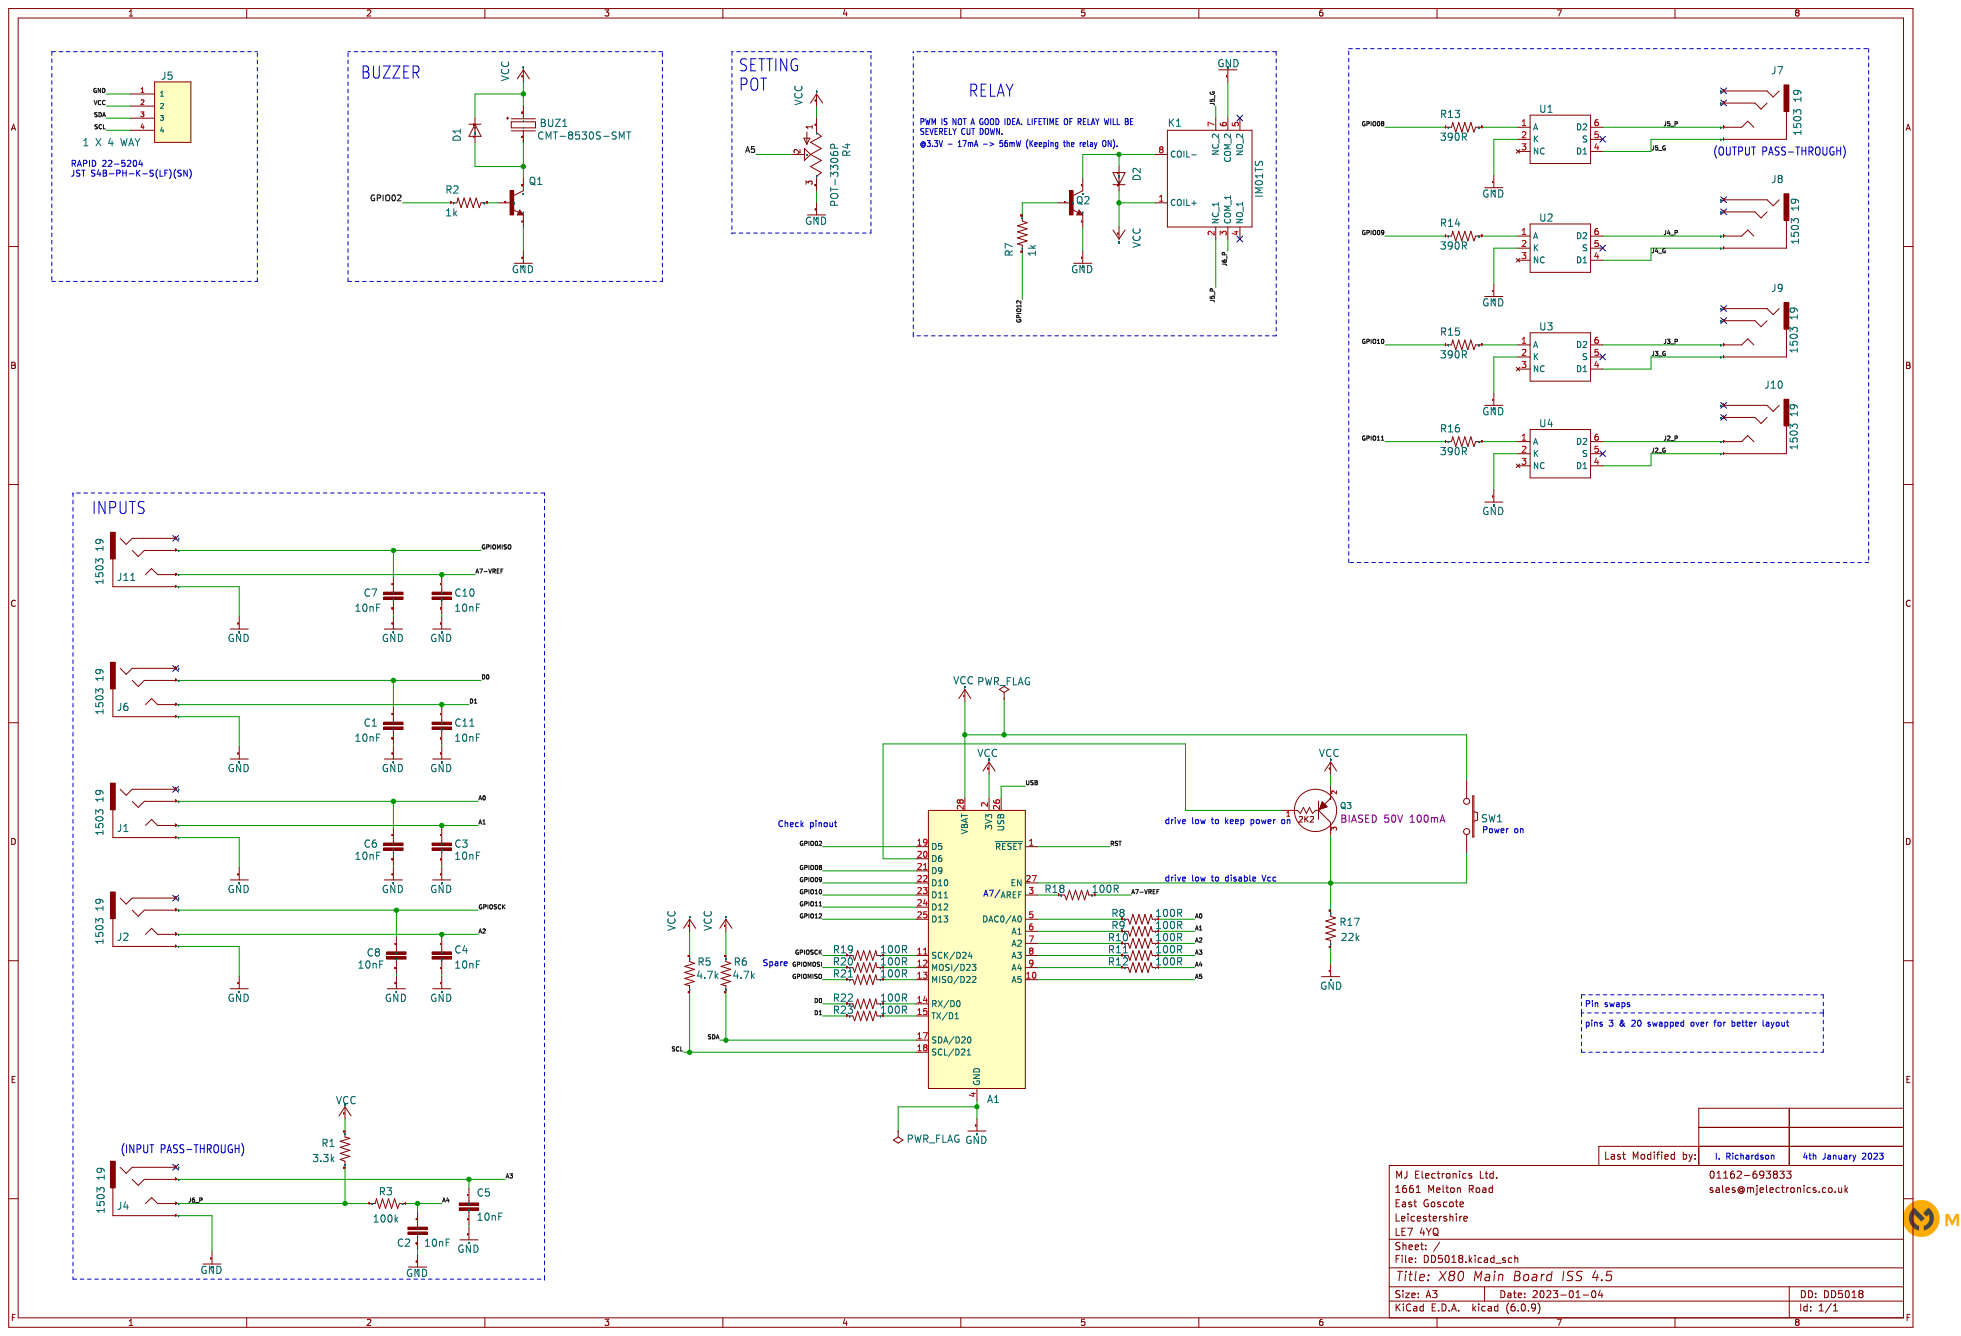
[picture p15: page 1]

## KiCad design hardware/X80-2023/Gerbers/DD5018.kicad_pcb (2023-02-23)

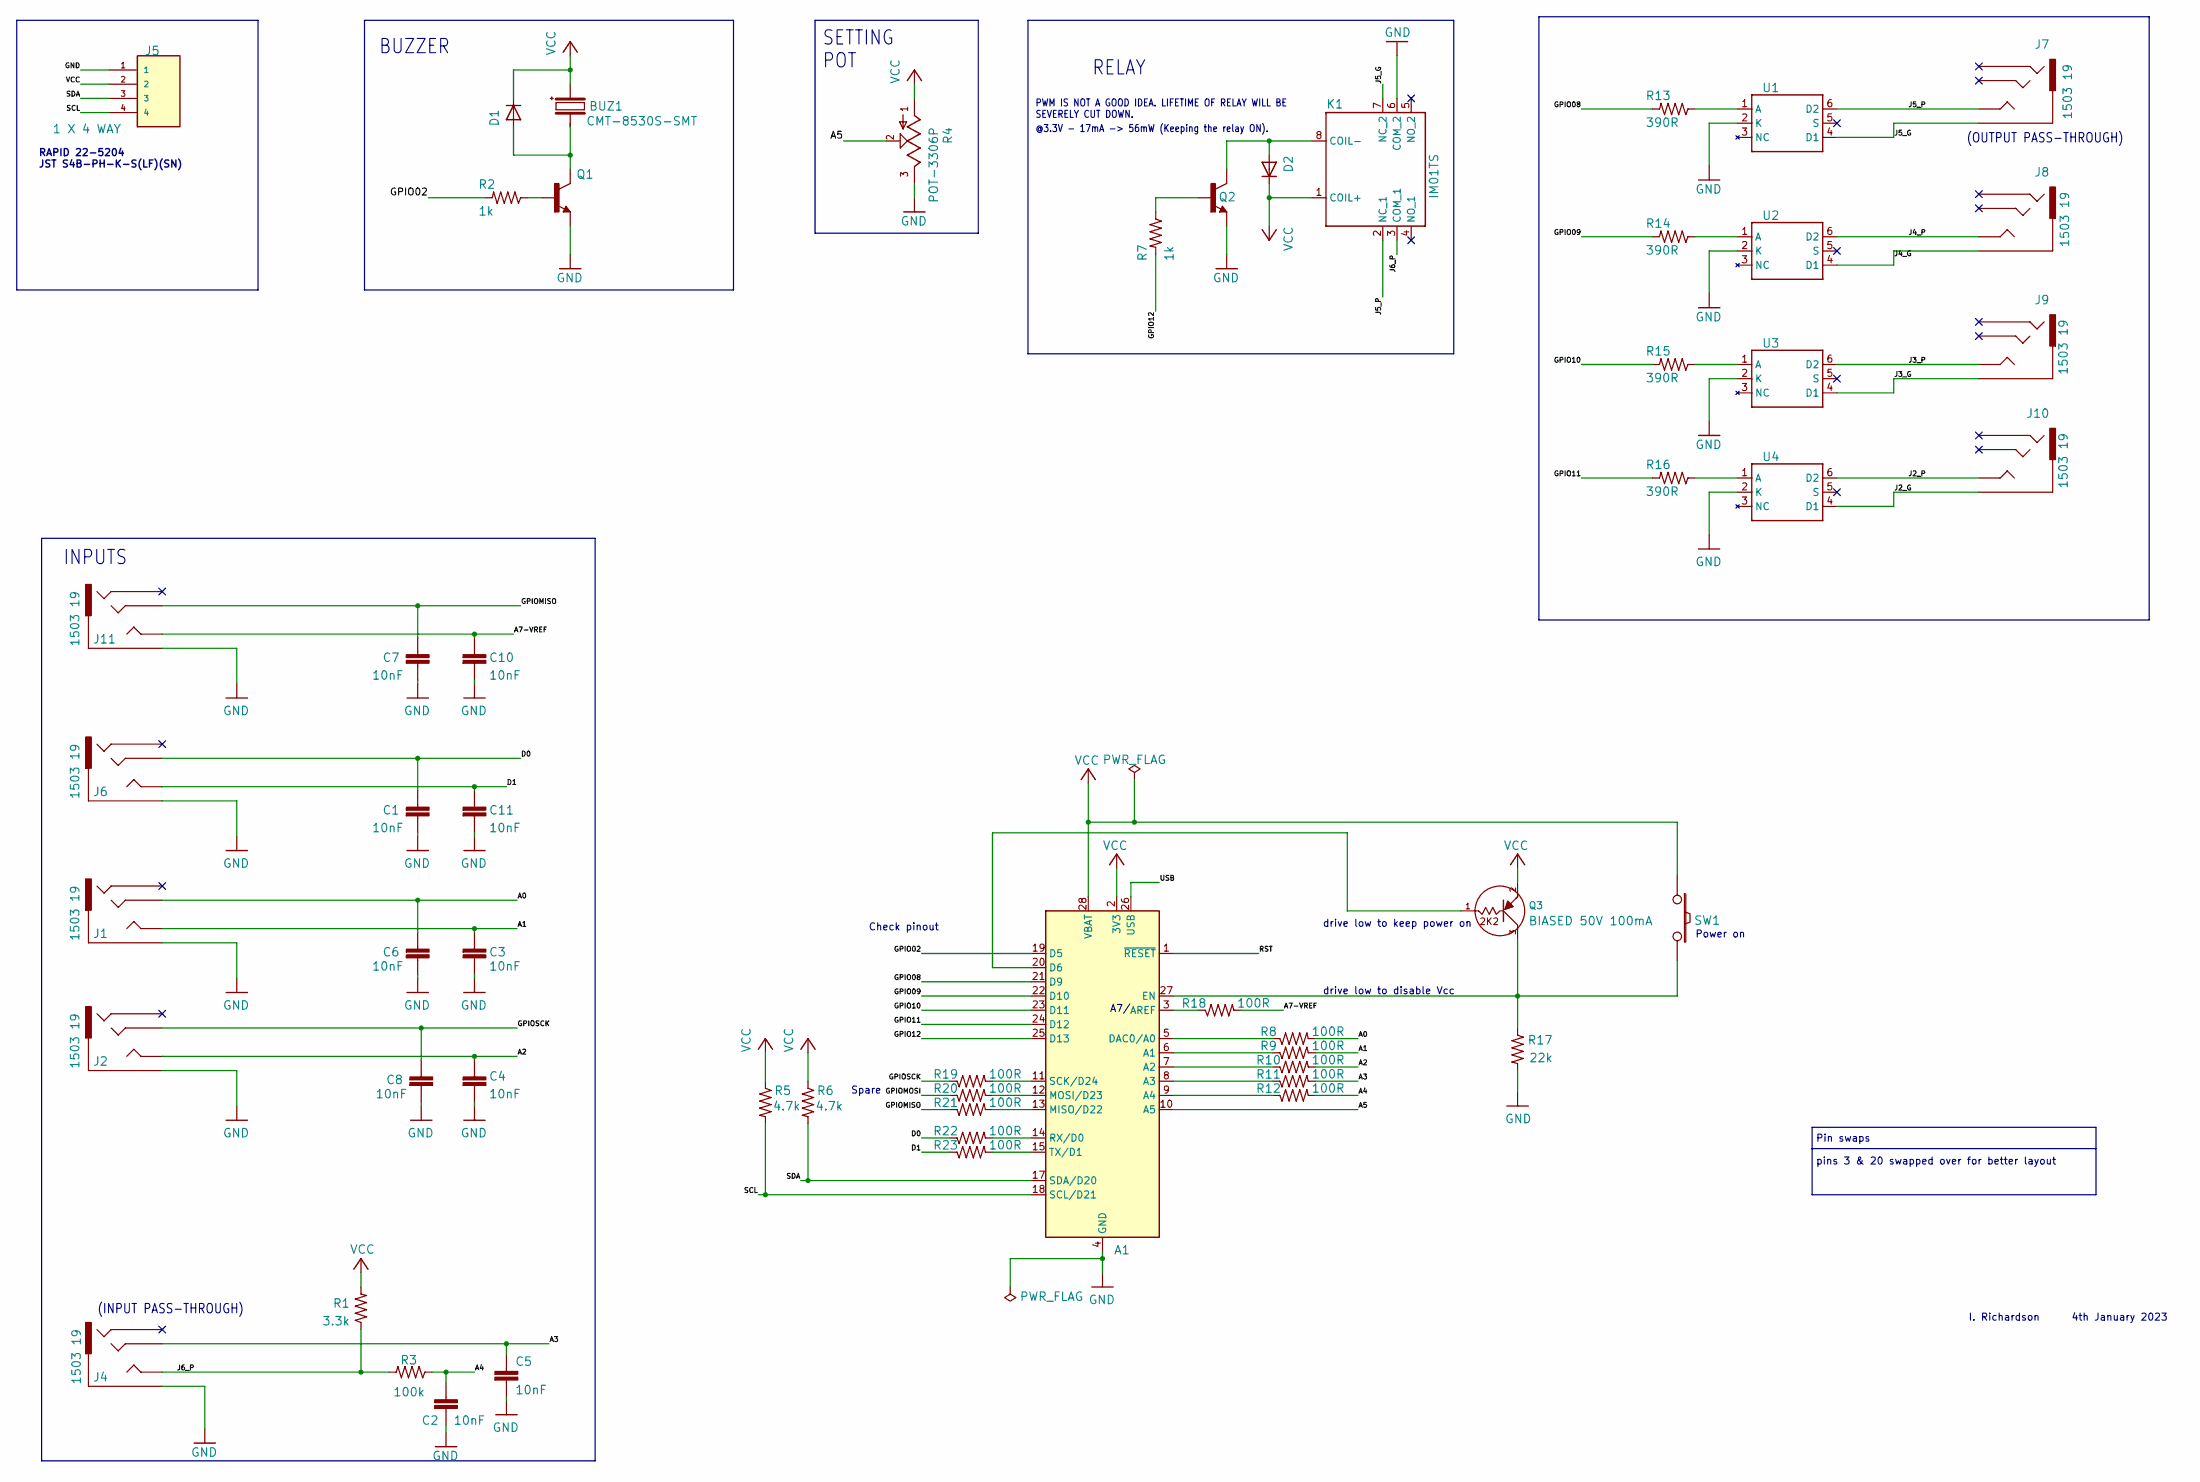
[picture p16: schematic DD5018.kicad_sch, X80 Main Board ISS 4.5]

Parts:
A1: Adafruit_Feather_M0_Basic_Proto; Adafruit_Feather
BUZ1: CMT-8530S-SMT; CMT8530SSMTTR
C1, C2, C3, C4, C5, C6, C7, C8, C10, C11: 10nF; CAPC1608X85
D1, D2: DIODE-SOD-123; SOD-123
J1, J2, J4, J6, J7, J8, J9, J10, J11: 1503 19; 1503-19
J5: 1 X 4 WAY; JST_S4B-PH-K-S(LF)(SN)
K1: IM01TS; IM03TS114620378
Q1, Q2: NPN-SOT-23; SOT-23
Q3: PNP-BIASED-2K2; SOT23-MMBT4401B; Part No MMUN2135LT1G
R1: 3.3k; R0603
R2, R7: 1k; R0603
R3: 100k; R0603
R4: POT-3306P; 3306P1103
R5, R6: 4.7k; R0603
R8, R9, R10, R11, R12, R18, R19, R20, R21, R22, R23: 100R; R0603
R13, R14, R15, R16: 390R; R0603
R17: 22k; R0603
SW1: SW_mini_SMT; DTSM-32S-B; Part No DTSM-32S-B
U1, U2, U3, U4: LH1500AT; DIP762W47P254L880H410Q6N

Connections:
/A0: C6.1, J1.3, R8.1
/A1: C3.1, J1.4, J1.5 (4), R9.1
/A2: C4.1, J2.4, J2.5 (4), R10.1
/A3: C5.1, J4.3, R11.1
/A4: C2.1, R3.2, R12.1
/A5: A1.10 (A5), R4.2
/A7-VREF: C10.1, J11.4, J11.5 (4), R18.1
/D0: C1.1, J6.3, R22.2
/D1: C11.1, J6.4, J6.5 (4), R23.2
/GPIO02: A1.19 (D5), R2.1
/GPIO08: A1.21 (D9), R13.1
/GPIO09: A1.22 (D10), R14.1
/GPIO10: A1.23 (D11), R15.1
/GPIO11: A1.24 (D12), R16.1
/GPIO12: A1.25 (D13), R7.1
/GPIOMISO: C7.1, J11.3, R21.2
/GPIOMOSI: R20.2
/GPIOSCK: C8.1, J2.3, R19.2
/J2_G: J10.1, U4.4 (D1)
/J2_P: J10.4, J10.5 (4), U4.6 (D2)
/J3_G: J9.1, U3.4 (D1)
/J3_P: J9.4, J9.5 (4), U3.6 (D2)
/J4_G: J8.1, U2.4 (D1)
/J4_P: J8.4, J8.5 (4), U2.6 (D2)
/J5_G: J7.1, K1.7 (NC_2), U1.4 (D1)
/J5_P: J7.4, J7.5 (4), K1.2 (NC_1), U1.6 (D2)
/J6_P: J4.4, J4.5 (4), K1.3 (COM_1), R1.2, R3.1
/RST: A1.1 (~RESET)
/SCL: A1.18 (SCL/D21), J5.4, R5.1
/SDA: A1.17 (SDA/D20), J5.3, R6.1
/USB: A1.26 (USB)
GND: A1.4 (GND), A1.16 (GND), C1.2, C2.2, C3.2, C4.2, C5.2, C6.2, C7.2, C8.2, C10.2, C11.2, J1.1, J2.1, J4.1, J5.1, J6.1, J11.1, K1.6 (COM_2), Q1.E, Q2.E, R4.3, R17.1, U1.2 (K), U2.2 (K), U3.2 (K), U4.2 (K)
unnamed: A1.3 (AREF), R18.2
unnamed: A1.5 (DAC0/A0), R8.2
unnamed: A1.6 (A1), R9.2
unnamed: A1.7 (A2), R10.2
unnamed: A1.8 (A3), R11.2
unnamed: A1.9 (A4), R12.2
unnamed: A1.11 (SCK/D24), R19.1
unnamed: A1.12 (MOSI/D23), R20.1
unnamed: A1.13 (MISO/D22), R21.1
unnamed: A1.14 (RX/D0), R22.1
unnamed: A1.15 (TX/D1), R23.1
unnamed: A1.20 (D6), Q3.1
unnamed: A1.27 (EN), Q3.3, R17.2, SW1.2
unnamed: BUZ1.3 (-), D1.A, Q1.C
unnamed: D2.A, K1.8 (COIL-), Q2.C
unnamed: Q1.B, R2.2
unnamed: Q2.B, R7.2
unnamed: R13.2, U1.1 (A)
unnamed: R14.2, U2.1 (A)
unnamed: R15.2, U3.1 (A)
unnamed: R16.2, U4.1 (A)
VCC: A1.2 (3V3), A1.28 (VBAT), BUZ1.2 (+), D1.C, D2.C, J5.2, K1.1 (COIL+), Q3.2, R1.1, R4.1, R5.2, R6.2, SW1.1

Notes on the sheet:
RELAY
Spare
PWM IS NOT A GOOD IDEA. LIFETIME OF RELAY WILL BE SEVERELY CUT DOWN.
(OUTPUT PASS-THROUGH)
(INPUT PASS-THROUGH)
4th January 2023
Power on
I. Richardson
RAPID 22-5204 JST S4B-PH-K-S(LF)(SN)
INPUTS
A7/
@3.3V - 17mA -> 56mW (Keeping the relay ON).
drive low to keep power on
drive low to disable Vcc
BUZZER
SETTING POT
Check pinout
Pin swaps pins 3 & 20 swapped over for better layout

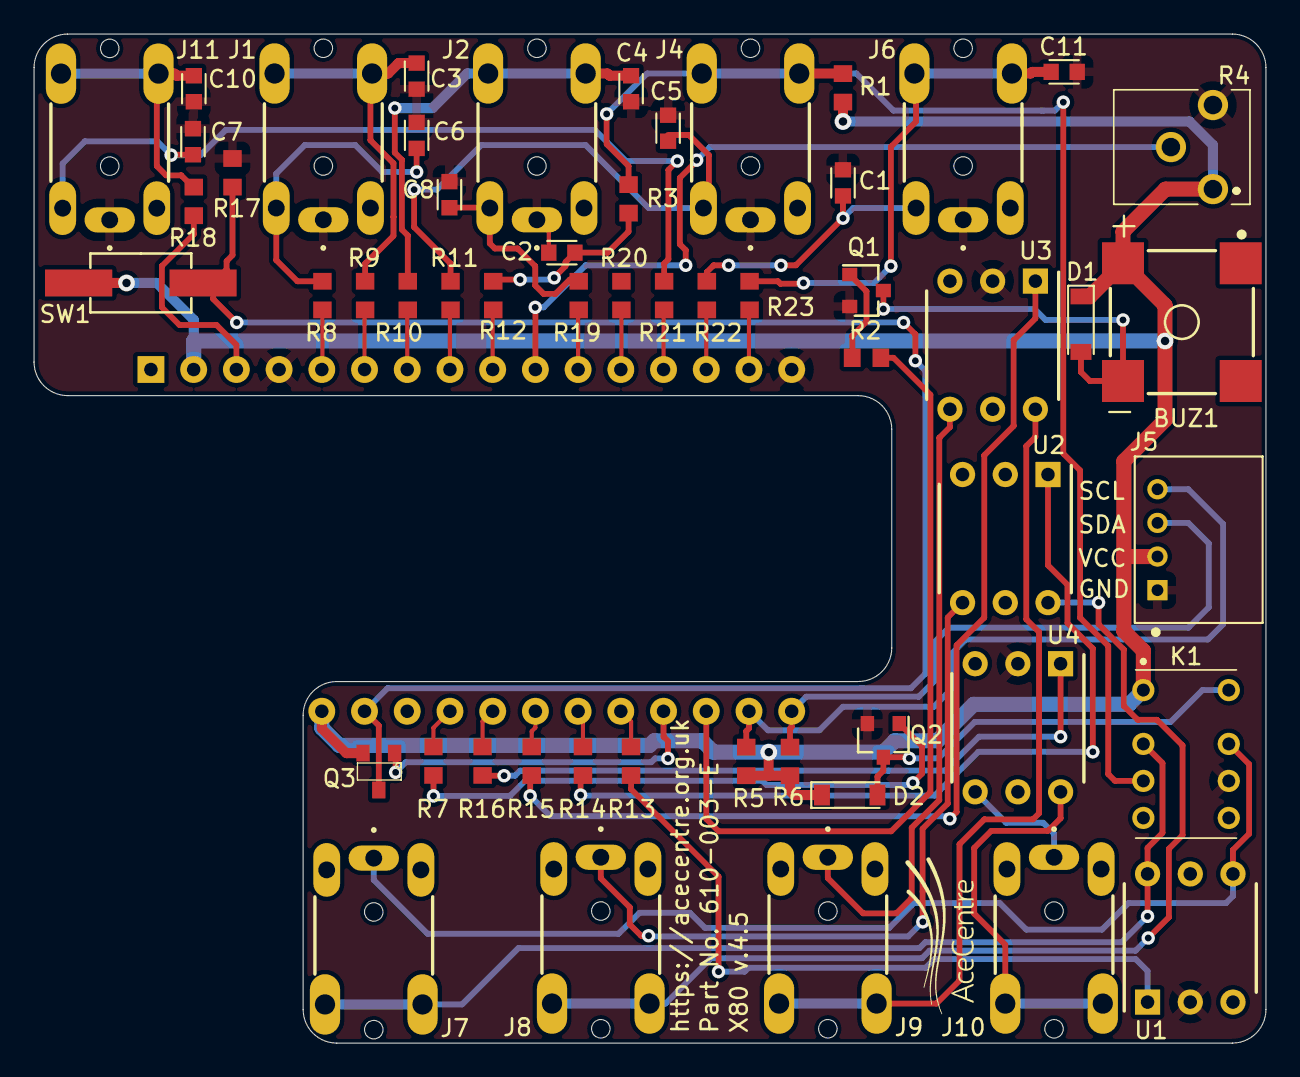
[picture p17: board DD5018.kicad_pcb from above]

Board: 2 copper layers, 73.2 x 60.0 mm, 56 parts (1 on the bottom side), 51 nets.

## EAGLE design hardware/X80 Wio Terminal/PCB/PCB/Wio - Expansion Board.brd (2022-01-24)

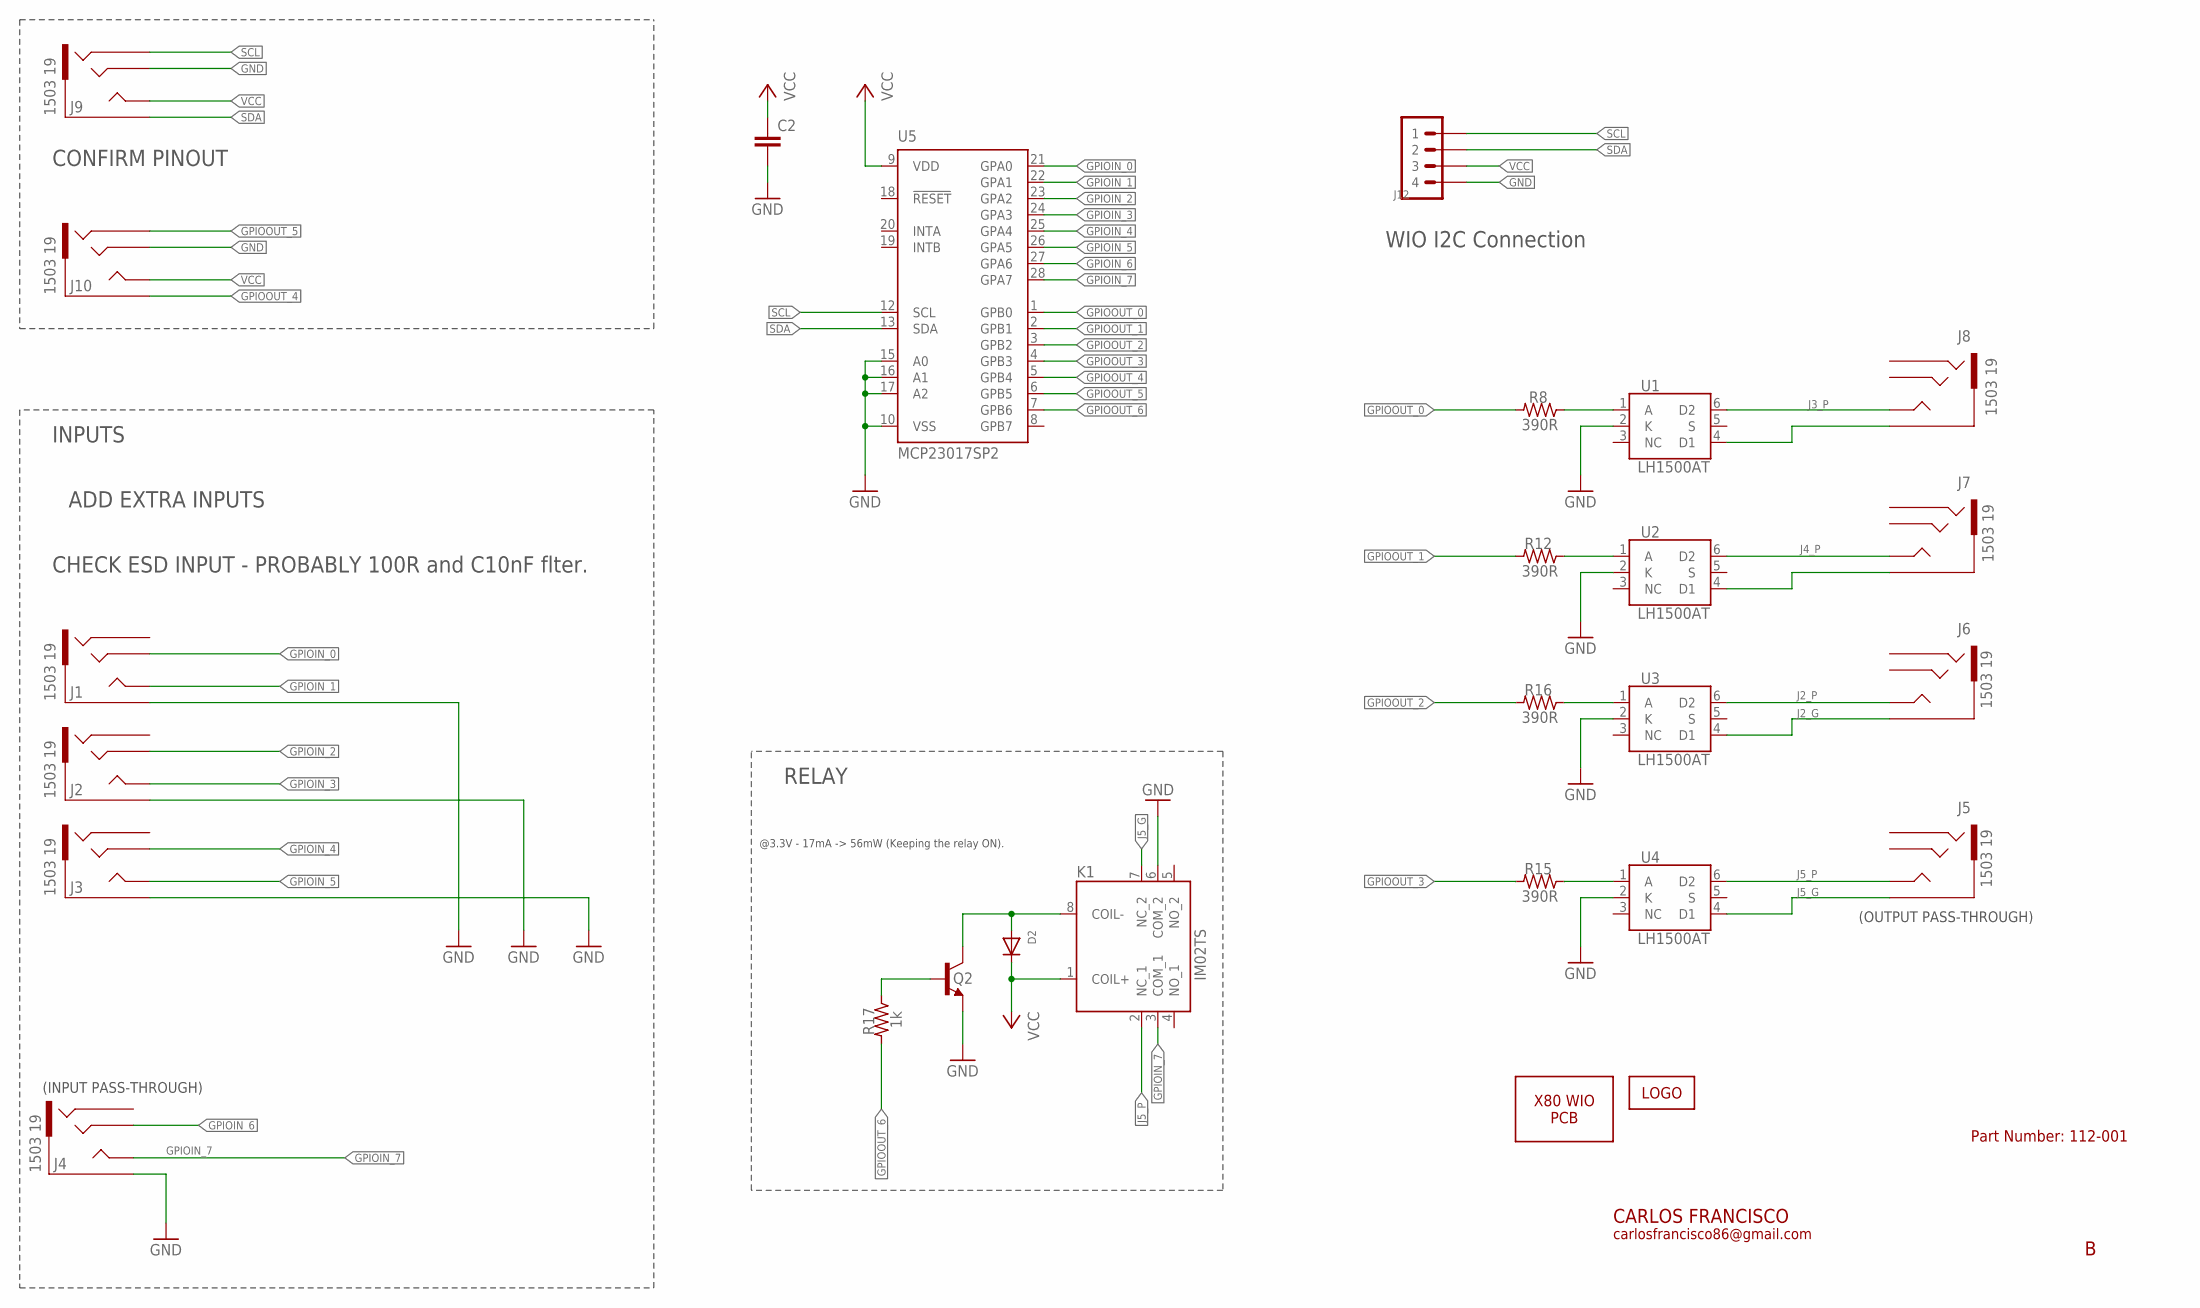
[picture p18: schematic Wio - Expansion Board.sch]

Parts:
C2: C-EU025-025X050; C025-025X050
D2: 1N4148; DO-1N4148
J1, J2, J3, J4, J5, J6, J7, J8, J9, J10: 1503 19; 1503-19
J12: 4P-2.0-90D; HW4-2.0-90D
K1: IM02TS; IM03TS114620378
LOGO1: LOGO-10MM; LOGO_10MM
PCB2: X80_WIO_PCB-WIO_PCB_V1; WIO_PCB
Q2: PN2222A; TO92-EBC-OVAL
R8, R12, R15, R16: 390R; 0204/7
R17: 1k; 0204/7
U1, U2, U3, U4: LH1500AT; DIP762W47P254L880H410Q6N
U5: MCP23017SP2; DIL28-3-ROUND

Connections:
GND: C2.2, J1.1, J2.1, J3.1, J4.1, J9.3, J10.3, J12.4, K1.6 (COM_2), Q2.E, U1.2 (K), U2.2 (K), U3.2 (K), U4.2 (K), U5.10 (VSS), U5.15 (A0), U5.16 (A1), U5.17 (A2)
GPIOIN_0: J1.3, U5.21 (GPA0)
GPIOIN_1: J1.4, J1.5 (4), U5.22 (GPA1)
GPIOIN_2: J2.3, U5.23 (GPA2)
GPIOIN_3: J2.4, J2.5 (4), U5.24 (GPA3)
GPIOIN_4: J3.3, U5.25 (GPA4)
GPIOIN_5: J3.4, J3.5 (4), U5.26 (GPA5)
GPIOIN_6: J4.3, U5.27 (GPA6)
GPIOIN_7: J4.4, J4.5 (4), K1.3 (COM_1), U5.28 (GPA7)
GPIOOUT_0: R8.1, U5.1 (GPB0)
GPIOOUT_1: R12.1, U5.2 (GPB1)
GPIOOUT_2: R16.1, U5.3 (GPB2)
GPIOOUT_3: R15.1, U5.4 (GPB3)
GPIOOUT_4: J10.1, U5.5 (GPB4)
GPIOOUT_5: J10.2, U5.6 (GPB5)
GPIOOUT_6: R17.1, U5.7 (GPB6)
J2_G: J6.1, U3.4 (D1)
J2_P: J6.4, J6.5 (4), U3.6 (D2)
J3_P: J8.4, J8.5 (4), U1.6 (D2)
J4_P: J7.4, J7.5 (4), U2.6 (D2)
J5_G: J5.1, K1.7 (NC_2), U4.4 (D1)
J5_P: J5.4, J5.5 (4), K1.2 (NC_1), U4.6 (D2)
unnamed: J8.1, U1.4 (D1)
unnamed: J7.1, U2.4 (D1)
unnamed: R8.2, U1.1 (A)
unnamed: R12.2, U2.1 (A)
unnamed: R16.2, U3.1 (A)
unnamed: R15.2, U4.1 (A)
unnamed: D2.A, K1.8 (COIL-), Q2.C
unnamed: Q2.B, R17.2
SCL: J9.2, J12.1, U5.12 (SCL)
SDA: J9.1, J12.2, U5.13 (SDA)
VCC: C2.1, D2.C, J9.4, J9.5 (4), J10.4, J10.5 (4), J12.3, K1.1 (COIL+), U5.9 (VDD)

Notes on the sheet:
CARLOS FRANCISCO
carlosfrancisco86@gmail.com
(INPUT PASS-THROUGH)
INPUTS
(OUTPUT PASS-THROUGH)
RELAY
Part Number: 112-001
@3.3V - 17mA -> 56mW (Keeping the relay ON).
CONFIRM PINOUT
ADD EXTRA INPUTS
WIO I2C Connection
CHECK ESD INPUT - PROBABLY 100R and C10nF flter.

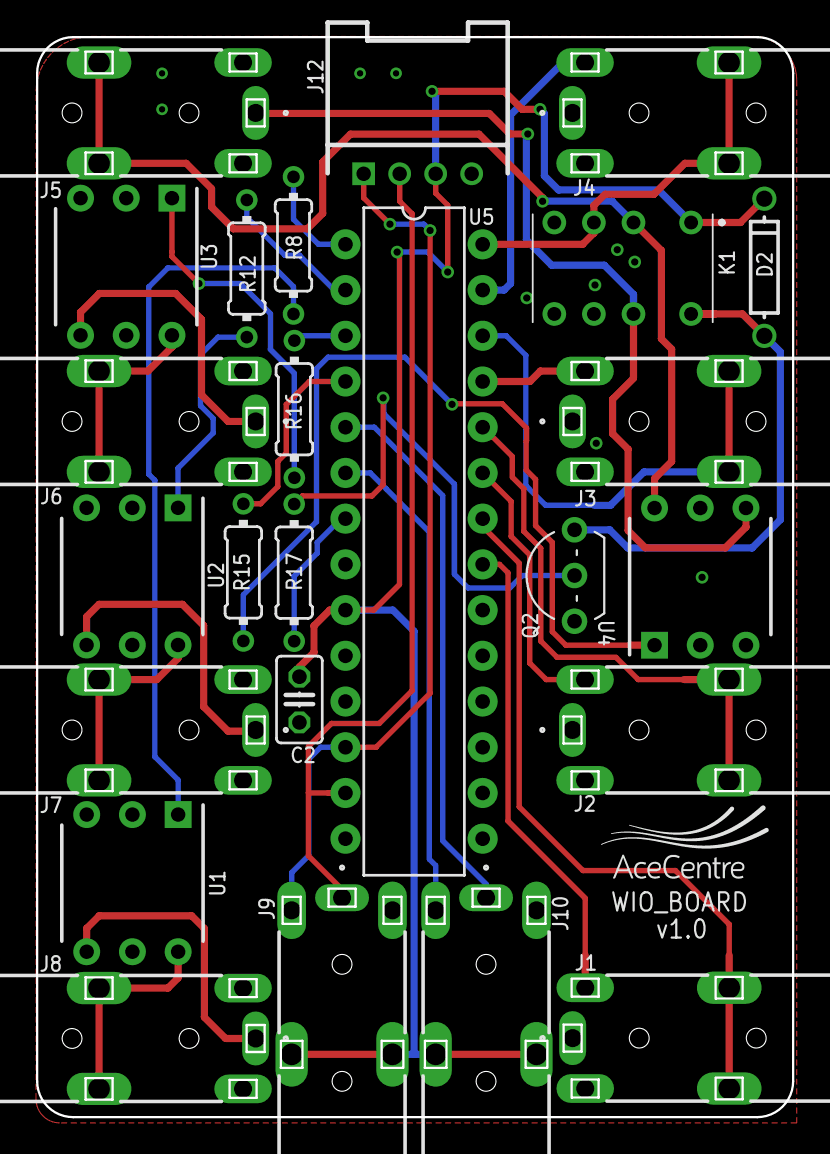
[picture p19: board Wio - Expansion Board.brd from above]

Board: 2 copper layers, 42.0 x 60.0 mm, 27 parts (0 on the bottom side), 33 nets.

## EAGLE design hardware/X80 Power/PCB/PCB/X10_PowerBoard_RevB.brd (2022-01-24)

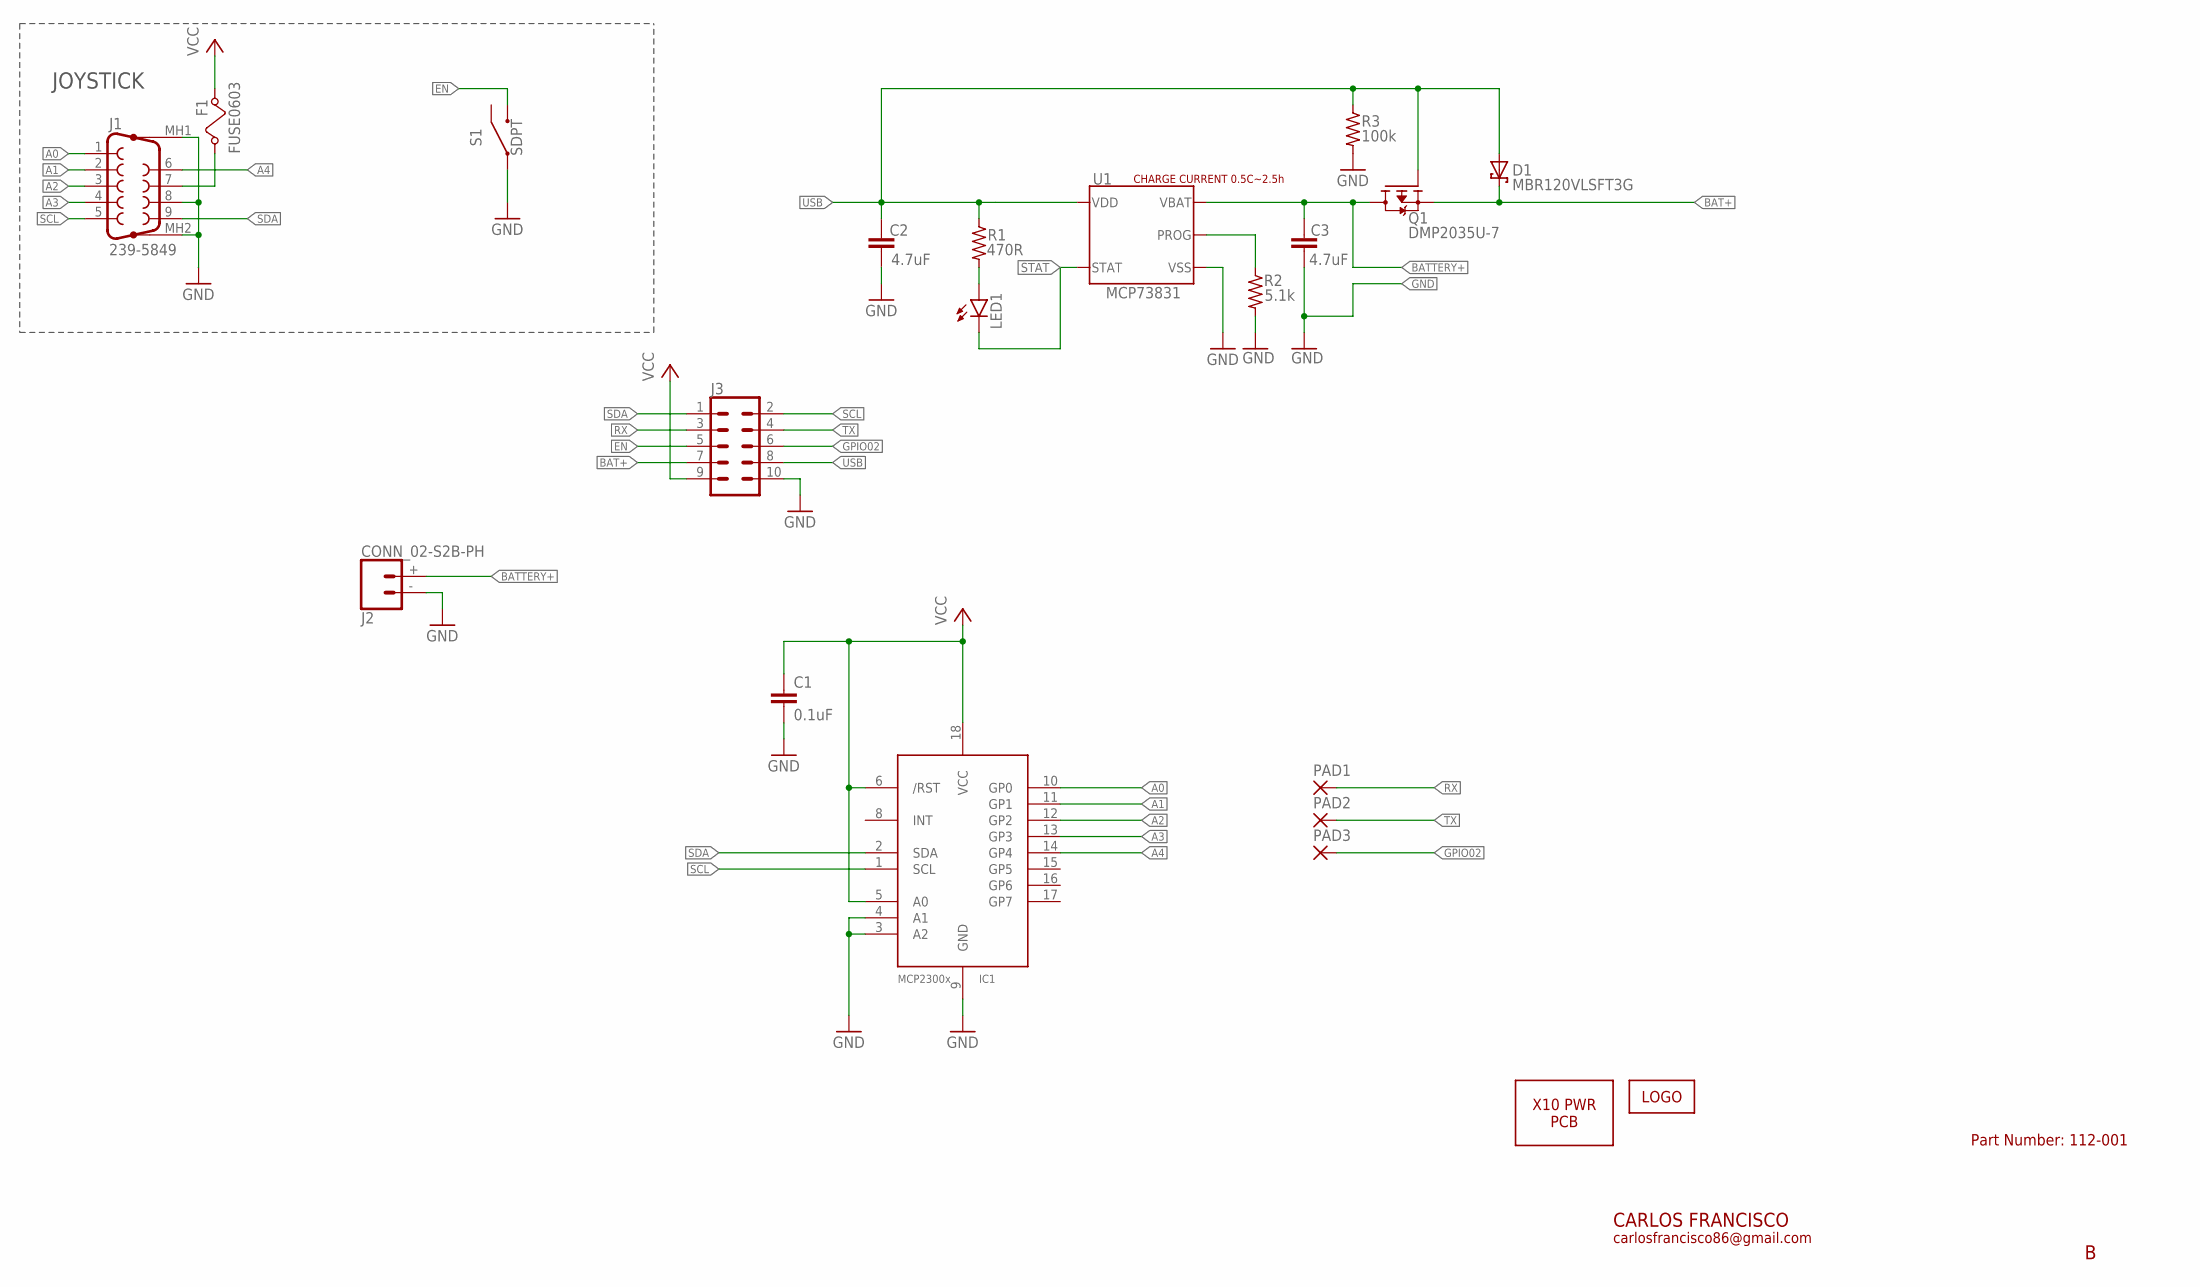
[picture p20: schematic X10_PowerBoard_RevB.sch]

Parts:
C1: 0.1uF; C0603
C2, C3: 4.7uF; CAPC1608X85
D1: MBR120VLSFT3G; SODFL3616X98N
F1: FUSE0603; FUSC1607X75N
IC1: MCP23008/P; DIL18
J1: 239-5849; DB9_PLUG_SLOT
J2: CONN_02-S2B-PH; S2B-PH-RA
J3: CONN2_05-HEADER; 2X5_HEADER
LED1: LEDSML0603; SML0603
LOGO1: LOGO-10MM; LOGO_10MM
PAD1, PAD2, PAD3: 1,6/0,8
PCB1: X10_PWR_PCB-X10_PWR_PCB; X10_POWER_PCB
Q1: DMP2035U-7; SOT95P230X110-3N
R1: 470R; RESC1608X60
R2: 5.1k; RESC1608X60
R3: 100k; RESC1608X60
S1: SDPT; OS102011MA1QN1
U1: MCP73831; SOT23-5P95_270X145L35X35N

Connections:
A0: IC1.10 (GP0), J1.1
A1: IC1.11 (GP1), J1.2
A2: IC1.12 (GP2), J1.3
A3: IC1.13 (GP3), J1.4
A4: IC1.14 (GP4), J1.6
BAT+: D1.K (C), J3.7, Q1.2 (S)
BATTERY+: C3.1, J2.+ (1), Q1.3 (D), U1.3 (VBAT)
EN: J3.5, S1.1
GND: C1.2, C2.2, C3.2, IC1.3 (A2), IC1.4 (A1), IC1.9 (GND), J1.8, J1.MH1 (G1), J1.MH2 (G2), J2.- (2), J3.10, R2.1, R3.1, S1.2, U1.2 (VSS)
GPIO02: J3.6, PAD3.1
unnamed: LED1.A, R1.1
unnamed: F1.1, J1.7
unnamed: R2.2, U1.5 (PROG)
RX: J3.3, PAD1.1
SCL: IC1.1 (SCL), J1.5, J3.2
SDA: IC1.2 (SDA), J1.9, J3.1
STAT: LED1.C, U1.1 (STAT)
TX: J3.4, PAD2.1
USB: C2.1, D1.A, J3.8, Q1.1 (G), R1.2, R3.2, U1.4 (VDD)
VCC: C1.1, F1.2, IC1.5 (A0), IC1.6 (/RST), IC1.18 (VCC), J3.9

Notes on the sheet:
CARLOS FRANCISCO
carlosfrancisco86@gmail.com
JOYSTICK
Part Number: 112-001
CHARGE CURRENT 0.5C~2.5h

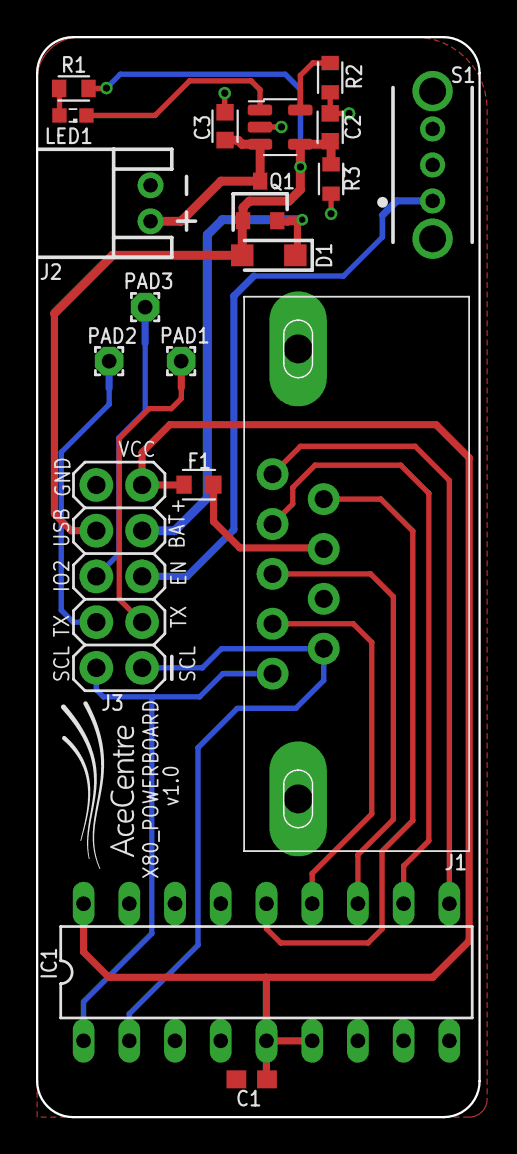
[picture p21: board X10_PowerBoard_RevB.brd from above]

Board: 2 copper layers, 24.6 x 60.0 mm, 21 parts (0 on the bottom side), 20 nets.

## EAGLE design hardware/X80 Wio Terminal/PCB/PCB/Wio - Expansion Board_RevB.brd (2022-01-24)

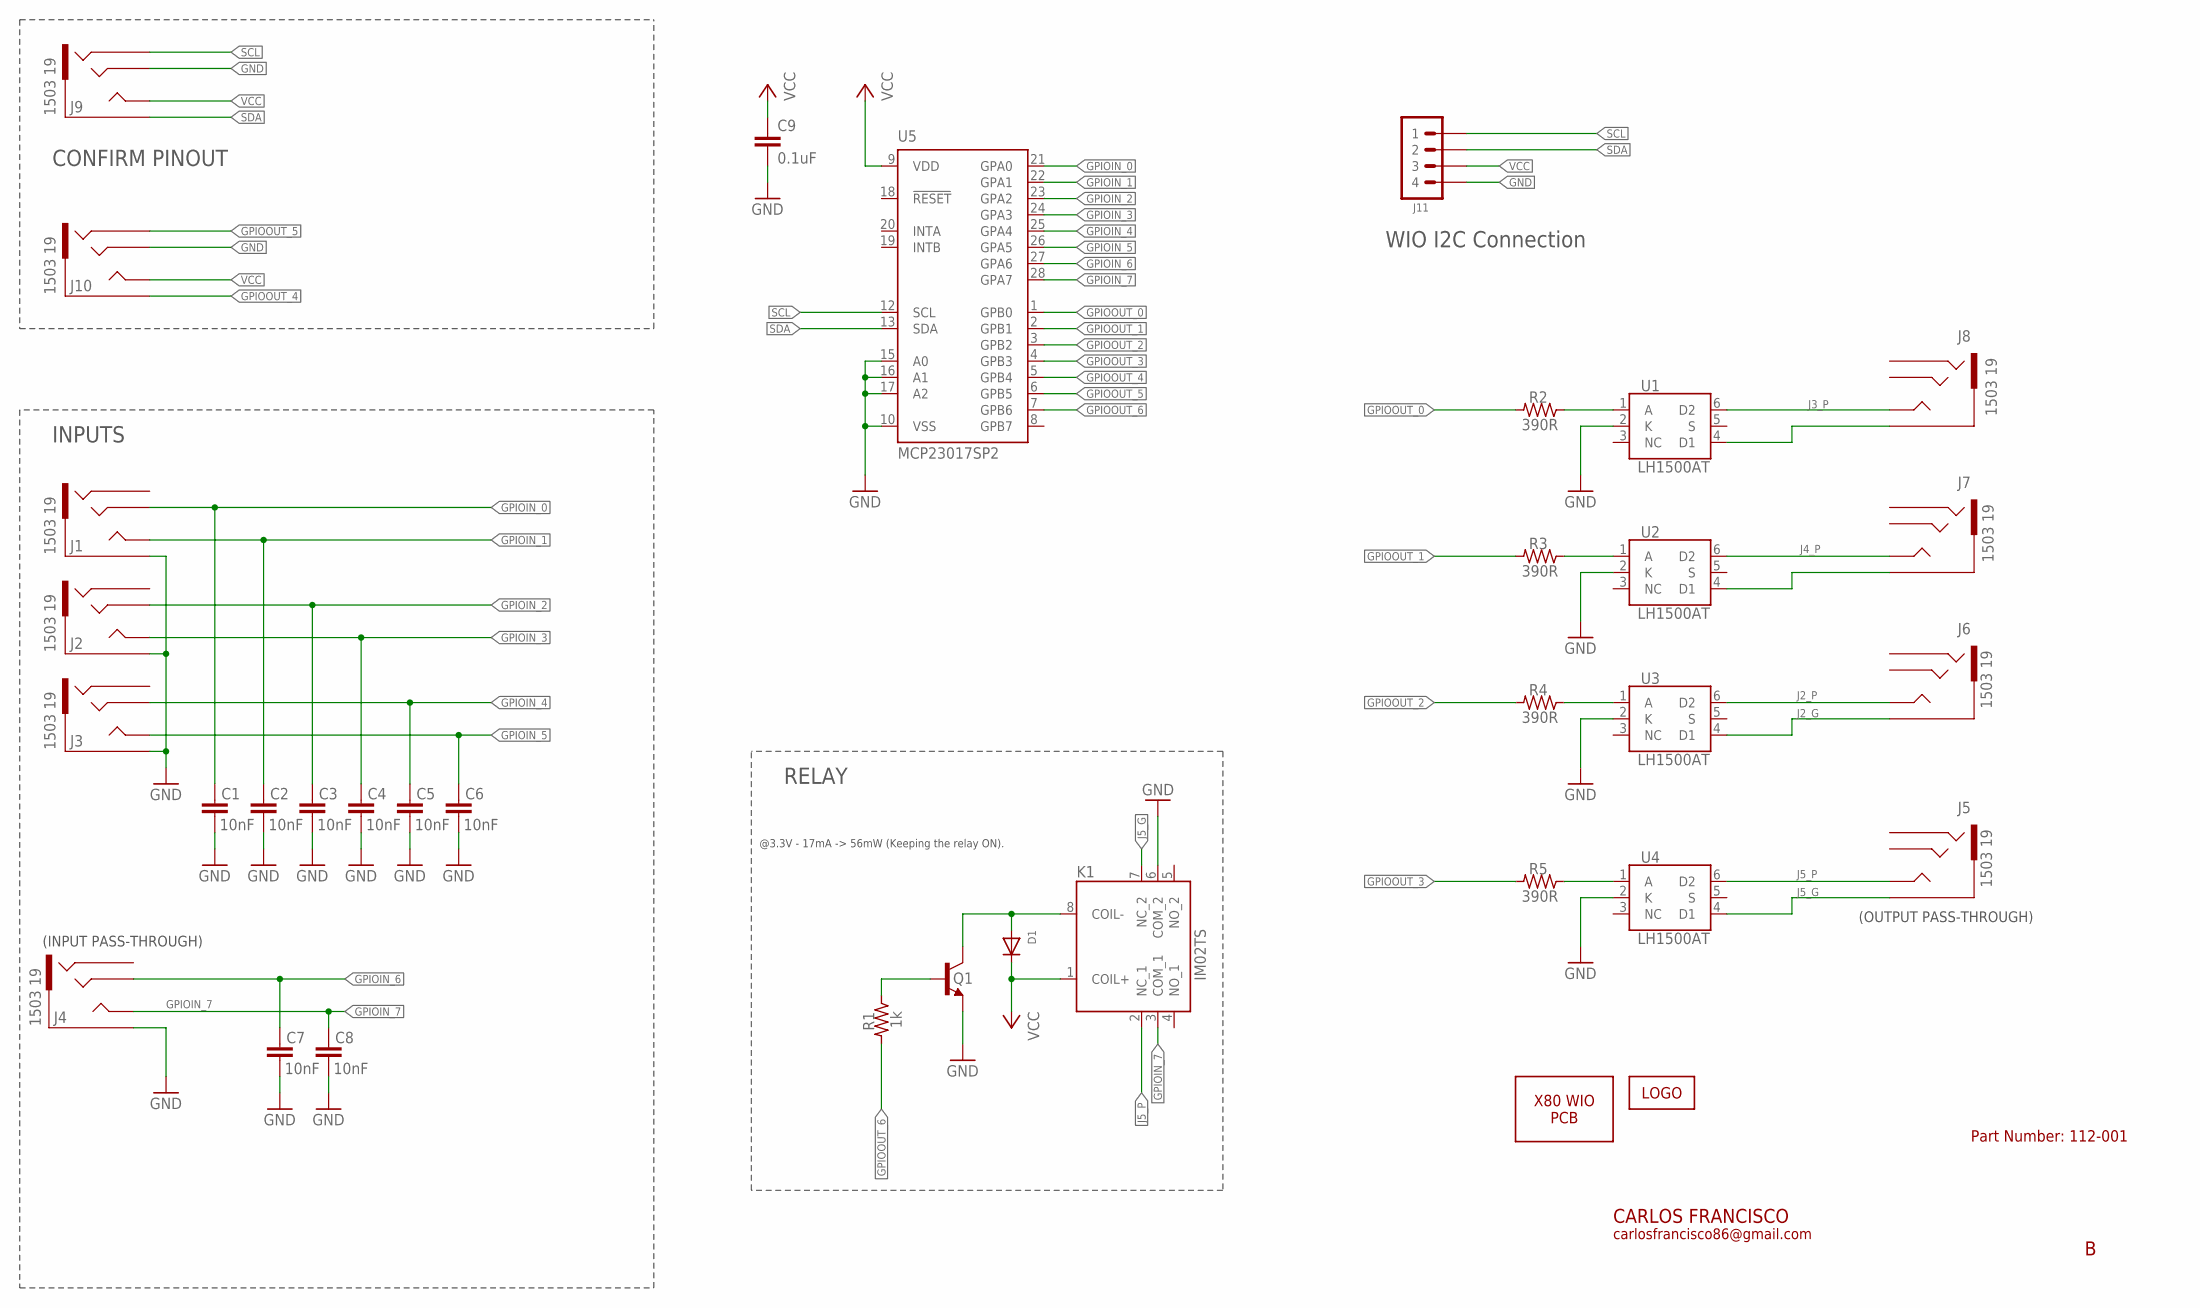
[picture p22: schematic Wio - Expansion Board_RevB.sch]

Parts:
C1, C2, C3, C4, C5, C6, C7, C8: 10nF; C025-024X044
C9: 0.1uF; C025-025X050
D1: 1N4148; DO-1N4148
J1, J2, J3, J4, J5, J6, J7, J8, J9, J10: 1503 19; 1503-19
J11: 4P-2.0-90D; HW4-2.0-90D
K1: IM02TS; IM03TS114620378
LOGO1: LOGO-10MM; LOGO_10MM
PCB2: X80_WIO_PCB-WIO_PCB_V1; WIO_PCB
Q1: PN2222A; TO92-EBC-OVAL
R1: 1k; 0204/7
R2, R3, R4, R5: 390R; 0204/7
U1, U2, U3, U4: LH1500AT; DIP762W47P254L880H410Q6N
U5: MCP23017SP2; DIL28-3-ROUND

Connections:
GND: C1.2, C2.2, C3.2, C4.2, C5.2, C6.2, C7.2, C8.2, C9.2, J1.1, J2.1, J3.1, J4.1, J9.3, J10.3, J11.4, K1.6 (COM_2), Q1.E, U1.2 (K), U2.2 (K), U3.2 (K), U4.2 (K), U5.10 (VSS), U5.15 (A0), U5.16 (A1), U5.17 (A2)
GPIOIN_0: C1.1, J1.3, U5.21 (GPA0)
GPIOIN_1: C2.1, J1.4, J1.5 (4), U5.22 (GPA1)
GPIOIN_2: C3.1, J2.3, U5.23 (GPA2)
GPIOIN_3: C4.1, J2.4, J2.5 (4), U5.24 (GPA3)
GPIOIN_4: C5.1, J3.3, U5.25 (GPA4)
GPIOIN_5: C6.1, J3.4, J3.5 (4), U5.26 (GPA5)
GPIOIN_6: C7.1, J4.3, U5.27 (GPA6)
GPIOIN_7: C8.1, J4.4, J4.5 (4), K1.3 (COM_1), U5.28 (GPA7)
GPIOOUT_0: R2.1, U5.1 (GPB0)
GPIOOUT_1: R3.1, U5.2 (GPB1)
GPIOOUT_2: R4.1, U5.3 (GPB2)
GPIOOUT_3: R5.1, U5.4 (GPB3)
GPIOOUT_4: J10.1, U5.5 (GPB4)
GPIOOUT_5: J10.2, U5.6 (GPB5)
GPIOOUT_6: R1.1, U5.7 (GPB6)
J2_G: J6.1, U3.4 (D1)
J2_P: J6.4, J6.5 (4), U3.6 (D2)
J3_P: J8.4, J8.5 (4), U1.6 (D2)
J4_P: J7.4, J7.5 (4), U2.6 (D2)
J5_G: J5.1, K1.7 (NC_2), U4.4 (D1)
J5_P: J5.4, J5.5 (4), K1.2 (NC_1), U4.6 (D2)
unnamed: J8.1, U1.4 (D1)
unnamed: J7.1, U2.4 (D1)
unnamed: R2.2, U1.1 (A)
unnamed: R3.2, U2.1 (A)
unnamed: R4.2, U3.1 (A)
unnamed: R5.2, U4.1 (A)
unnamed: D1.A, K1.8 (COIL-), Q1.C
unnamed: Q1.B, R1.2
SCL: J9.2, J11.1, U5.12 (SCL)
SDA: J9.1, J11.2, U5.13 (SDA)
VCC: C9.1, D1.C, J9.4, J9.5 (4), J10.4, J10.5 (4), J11.3, K1.1 (COIL+), U5.9 (VDD)

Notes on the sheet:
CARLOS FRANCISCO
carlosfrancisco86@gmail.com
(INPUT PASS-THROUGH)
INPUTS
(OUTPUT PASS-THROUGH)
RELAY
Part Number: 112-001
@3.3V - 17mA -> 56mW (Keeping the relay ON).
CONFIRM PINOUT
WIO I2C Connection

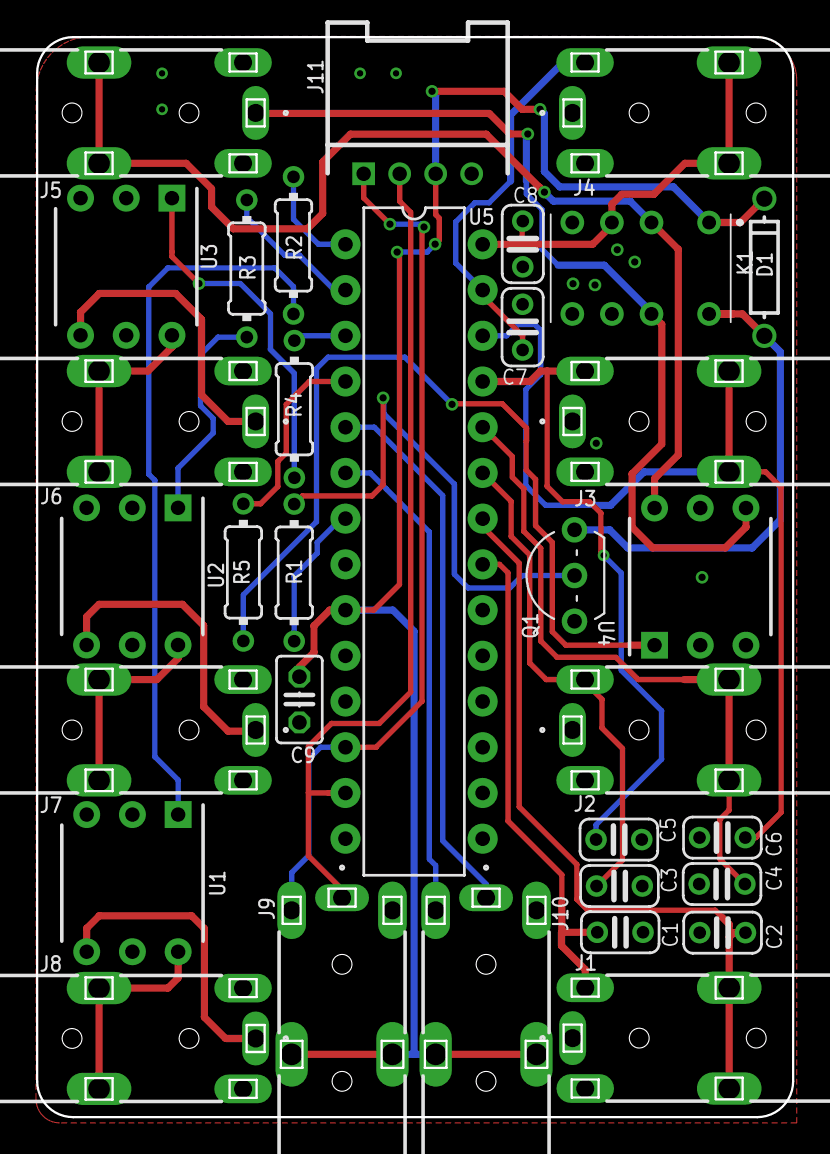
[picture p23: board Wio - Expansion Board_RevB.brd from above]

Board: 2 copper layers, 42.0 x 60.0 mm, 35 parts (1 on the bottom side), 33 nets.

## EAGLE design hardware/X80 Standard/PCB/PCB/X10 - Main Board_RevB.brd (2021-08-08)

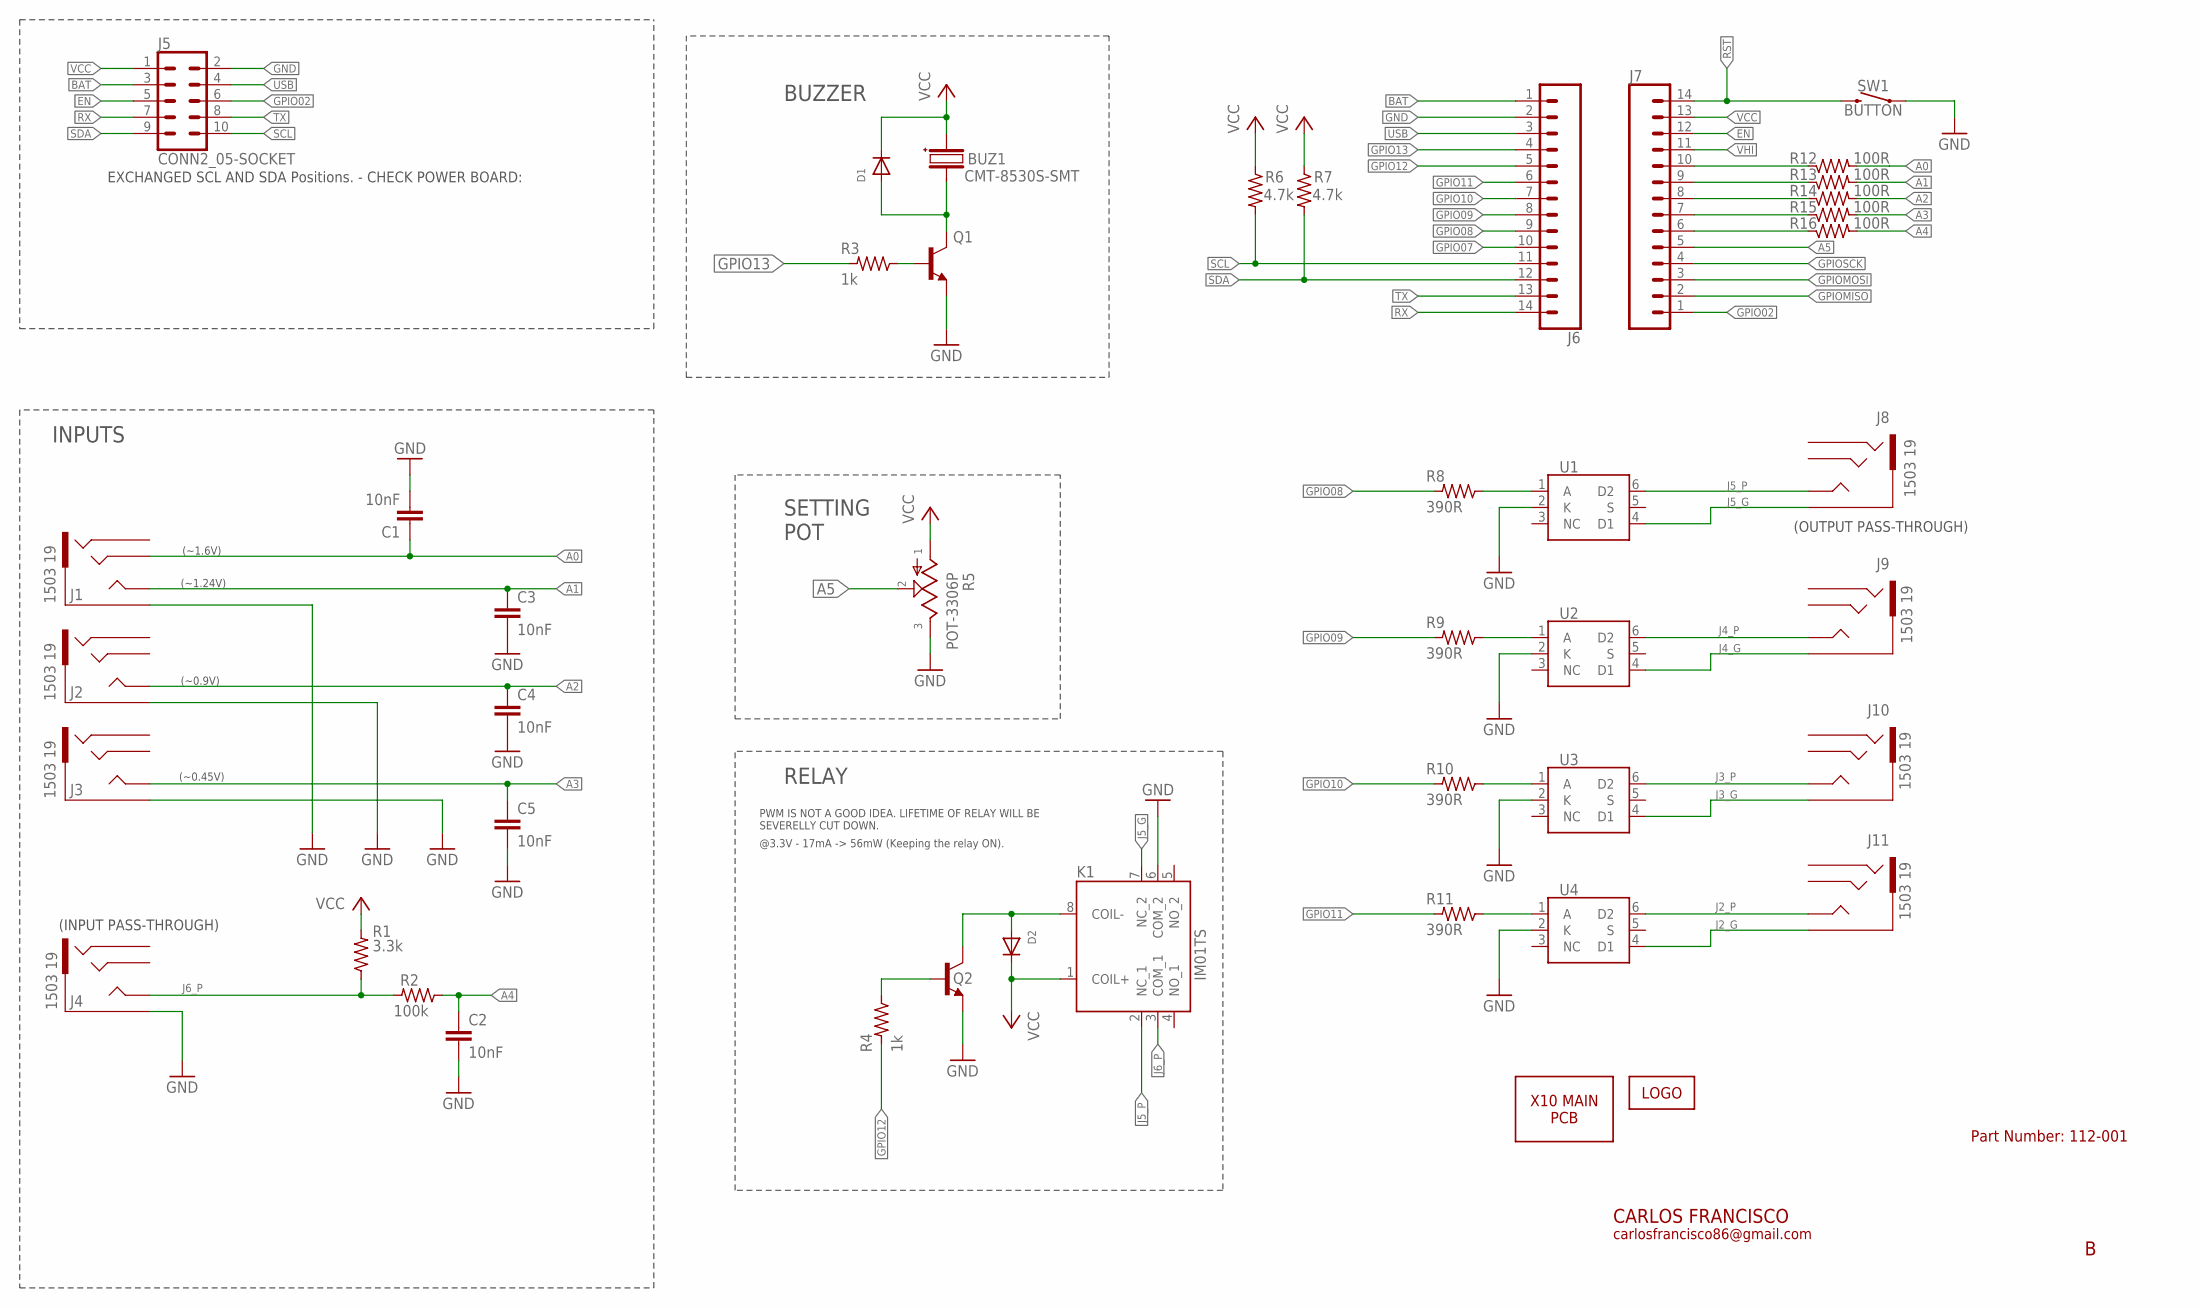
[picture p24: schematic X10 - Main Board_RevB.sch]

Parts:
BUZ1: CMT-8530S-SMT; CMT8530SSMTTR
C1, C2, C3, C4, C5: 10nF; CAPC1608X85
D1, D2: DIODE-SOD-123; SOD-123
J1, J2, J3, J4, J8, J9, J10, J11: 1503 19; 1503-19
J5: CONN2_05-SOCKET; 2X5_SOCKET
J6, J7: CONN_14; 1X14
K1: IM01TS; IM03TS114620378
LOGO1: LOGO-10MM; LOGO_10MM
PCB1: X10_MAIN_PCB-X10_MAIN; X10_MAIN_PCB
Q1, Q2: NPN-SOT-23; SOT-23
R1: 3.3k; R0603
R2: 100k; R0603
R3, R4: 1k; R0603
R5: POT-3306P; 3306P1103
R6, R7: 4.7k; R0603
R8, R9, R10, R11: 390R; R0603
R12, R13, R14, R15, R16: 100R; R0603
SW1: BUTTON; SERIES95C_RA
U1, U2, U3, U4: LH1500AT; DIP762W47P254L880H410Q6N

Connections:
A0: C1.1, J1.3, R12.1
A1: C3.1, J1.4, J1.5 (4), R13.1
A2: C4.1, J2.4, J2.5 (4), R14.1
A3: C5.1, J3.4, J3.5 (4), R15.1
A4: C2.1, R2.2, R16.1
A4_R: J7.6, R16.2
A5: J7.5, R5.2
BAT: J5.3, J6.1
BUZ_CTRL_R: Q1.B, R3.2
EN: J5.5, J7.12
GND: C1.2, C2.2, C3.2, C4.2, C5.2, J1.1, J2.1, J3.1, J4.1, J5.2, J6.2, K1.6 (COM_2), Q1.E, Q2.E, R5.3, SW1.T1 (1), U1.2 (K), U2.2 (K), U3.2 (K), U4.2 (K)
GPIO02: J5.6, J7.1
GPIO07: J6.10
GPIO08: J6.9, R8.1
GPIO09: J6.8, R9.1
GPIO10: J6.7, R10.1
GPIO11: J6.6, R11.1
GPIO12: J6.5, R4.1
GPIO13: J6.4, R3.1
GPIOMISO: J7.2
GPIOMOSI: J7.3
GPIOSCK: J7.4
J2_G: J11.1, U4.4 (D1)
J2_P: J11.4, J11.5 (4), U4.6 (D2)
J3_G: J10.1, U3.4 (D1)
J3_P: J10.4, J10.5 (4), U3.6 (D2)
J4_G: J9.1, U2.4 (D1)
J4_P: J9.4, J9.5 (4), U2.6 (D2)
J5_G: J8.1, K1.7 (NC_2), U1.4 (D1)
J5_P: J8.4, J8.5 (4), K1.2 (NC_1), U1.6 (D2)
J6_P: J4.4, J4.5 (4), K1.3 (COM_1), R1.2, R2.1
unnamed: BUZ1.3 (-), D1.A, Q1.C
unnamed: J7.10, R12.2
unnamed: J7.9, R13.2
unnamed: J7.8, R14.2
unnamed: J7.7, R15.2
unnamed: R8.2, U1.1 (A)
unnamed: R9.2, U2.1 (A)
unnamed: R11.2, U4.1 (A)
unnamed: R10.2, U3.1 (A)
unnamed: D2.A, K1.8 (COIL-), Q2.C
unnamed: Q2.B, R4.2
RST: J7.14, SW1.T2 (2)
RX: J5.7, J6.14
SCL: J5.10, J6.11, R6.1
SDA: J5.9, J6.12, R7.1
TX: J5.8, J6.13
USB: J5.4, J6.3
VCC: BUZ1.2 (+), D1.C, D2.C, J5.1, J7.13, K1.1 (COIL+), R1.1, R5.1, R6.2, R7.2
VHI: J7.11

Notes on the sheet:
CARLOS FRANCISCO
carlosfrancisco86@gmail.com
BUZZER
SETTING POT
(INPUT PASS-THROUGH)
INPUTS
(OUTPUT PASS-THROUGH)
RELAY
PWM IS NOT A GOOD IDEA. LIFETIME OF RELAY WILL BE SEVERELLY CUT DOWN.
Part Number: 112-001
@3.3V - 17mA -> 56mW (Keeping the relay ON).
(~1.6V)
(~1.24V)
(~0.9V)
(~0.45V)
EXCHANGED SCL AND SDA Positions. - CHECK POWER BOARD:

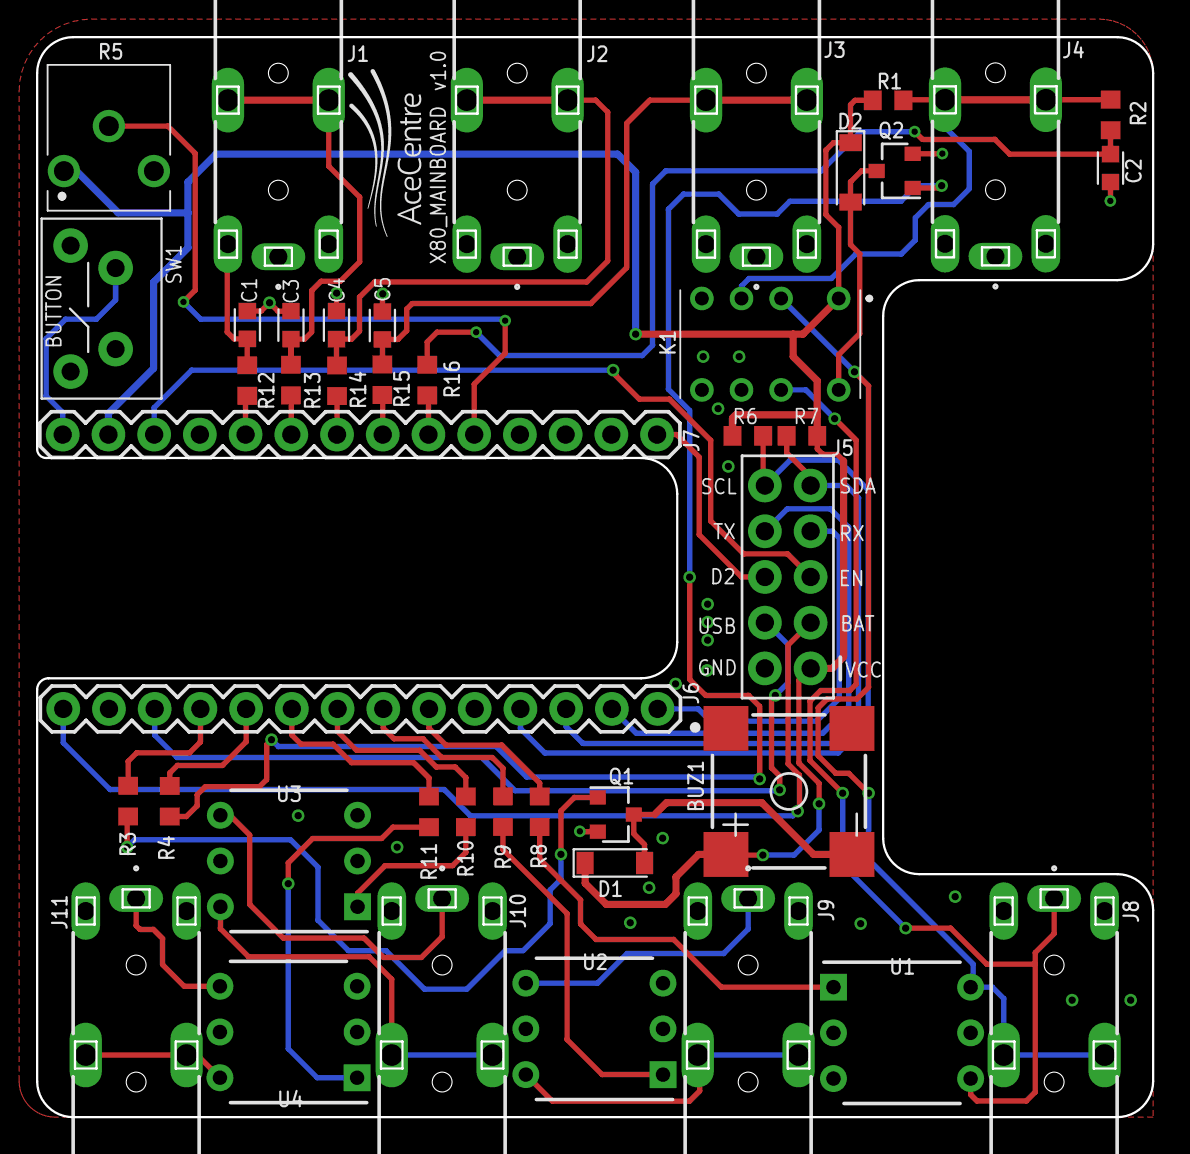
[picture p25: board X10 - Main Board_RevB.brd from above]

Board: 2 copper layers, 62.0 x 60.0 mm, 45 parts (0 on the bottom side), 45 nets.

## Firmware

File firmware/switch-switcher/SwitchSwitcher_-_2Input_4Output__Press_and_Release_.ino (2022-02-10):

/*
 * This code is an adaptation of the code found here:
  http://jmsarduino.blogspot.com/2009/05/click-for-press-and-hold-for-b.html
  

This program has 2 input buttons that always operate in the same output. Button 1 is the only button that changes the output
   
*/

#define buttonPin1 3 // analog input pin to use as a digital input
#define buttonPin2 4 // analog input pin to use as a digital input

//OUTPUT 1 LEDs
#define ledPin1 6 // digital output pin for LED 1 indicator - blue LED
#define ledPin2 7 // digital output pin for LED 2 indicator - green LED
#define ledPin3 9 // digital output pin for LED 3 indicator - red LED 
#define ledPin4 10 // digital output pin for LED 4 indicator - yellow LED

//OUTPUT 2 LEDs
#define ledPin5 5 // digital output pin for LED 5 indicator - blue LED
#define ledPin6 8 // digital output pin for LED 6 indicator - green LED
#define ledPin7 11 // digital output pin for LED 7 indicator - red LED 
#define ledPin8 12 // digital output pin for LED 8 indicator - yellow LED

#define debounce 20 // ms debounce period to prevent flickering when pressing or releasing the button
#define holdTime 2000 // ms hold period: how long to wait for press+hold event

boolean PressModeOn = true; // this will determine if the program will work in PRESS mode
boolean ReleaseModeOn = false; // this will determine if the program will work in RELEASE mode

// Buttons variables
int button1Val = 0; // value read from button 1
int button1Last = 0; // buffered value of the button1's previous state
int button2Val = 0; // value read from button 2
int button2Last = 0; // buffered value of the button2's previous state

long btn1DnTime; // time the button 1 was pressed down
long btn1UpTime; // time the button 1 was released
long btn2DnTime; // time the button 2 was pressed down
long btn2UpTime; // time the button 2 was released

boolean ignore1Up = false; // whether to ignore the button 1 release because the click+hold was triggered
boolean ignore2Up = false; // whether to ignore the button 2 release because the click+hold was triggered

// LED variables
boolean ledVal1 = false; // state of LED 1
boolean ledVal2 = false; // state of LED 2
boolean ledVal3 = false; // state of LED 3
boolean ledVal4 = false; // state of LED 4
boolean ledVal5 = false; // state of LED 5
boolean ledVal6 = false; // state of LED 6
boolean ledVal7 = false; // state of LED 7
boolean ledVal8 = false; // state of LED 8


// OUTPUT variables
boolean output1 = true; // output 1 set as default
boolean output2 = false; // output 2 set disabled
boolean output3 = false; // output 3 set disabled
boolean output4 = false; // output 4 set disabled

//=================================================

// Output events to trigger 

// ######################## Button 1 events ###########################
void event1()
{
digitalWrite(ledPin1, HIGH);
delay(200);
digitalWrite(ledPin1, LOW);
}

void event2()
{
digitalWrite(ledPin2, HIGH);
delay(200);
digitalWrite(ledPin2, LOW);
}

void event3()
{
digitalWrite(ledPin3, HIGH);
delay(200);
digitalWrite(ledPin3, LOW);
}

void event4()
{
digitalWrite(ledPin4, HIGH);
delay(200);
digitalWrite(ledPin4, LOW);
}

// ######################## Button 2 events ###########################
void event5()
{
digitalWrite(ledPin5, HIGH);
delay(200);
digitalWrite(ledPin5, LOW);
}

void event6()
{
digitalWrite(ledPin6, HIGH);
delay(200);
digitalWrite(ledPin6, LOW);
}

void event7()
{
digitalWrite(ledPin7, HIGH);
delay(200);
digitalWrite(ledPin7, LOW);
}

void event8()
{
digitalWrite(ledPin8, HIGH);
delay(200);
digitalWrite(ledPin8, LOW);
}


//############### Mode change event ###############

void eventModeChange()
{
digitalWrite(LED_BUILTIN, HIGH);
delay (100);
digitalWrite(LED_BUILTIN, LOW);
}

//=================================================


void setup()
{

// Set button input 1 and 2 pins
pinMode(buttonPin1, INPUT);
digitalWrite(buttonPin1, HIGH );
pinMode(buttonPin2, INPUT);
digitalWrite(buttonPin2, HIGH );

// Set LED output pins
pinMode(ledPin1, OUTPUT);
digitalWrite(ledPin1, ledVal1);
pinMode(ledPin2, OUTPUT);
digitalWrite(ledPin2, ledVal2);
pinMode(ledPin3, OUTPUT);
digitalWrite(ledPin3, ledVal3);
pinMode(ledPin4, OUTPUT);
digitalWrite(ledPin4, ledVal4);
pinMode(ledPin5, OUTPUT);
digitalWrite(ledPin5, ledVal5);
pinMode(ledPin6, OUTPUT);
digitalWrite(ledPin6, ledVal6);
pinMode(ledPin7, OUTPUT);
digitalWrite(ledPin7, ledVal7);
pinMode(ledPin8, OUTPUT);
digitalWrite(ledPin8, ledVal8);

pinMode(LED_BUILTIN, OUTPUT);
digitalWrite(LED_BUILTIN, LOW);

}


//=================================================


void loop()
{

// Read the state of the buttons
button1Val = digitalRead(buttonPin1);
button2Val = digitalRead(buttonPin2);

// Test for buttons pressed and store the down time
if (button1Val == LOW && button1Last == HIGH && (millis() - btn1UpTime) > long(debounce))
  {
  btn1DnTime = millis();
  }

if (button2Val == LOW && button2Last == HIGH && (millis() - btn2UpTime) > long(debounce))
  {
  btn2DnTime = millis();
  }


// ****************************************** CODE FOR PRESS MODE **************************************************************

if (PressModeOn == true){

// ################## OUTPUTs 1 - 4 for button 1 #################
  if (button1Val == LOW && button1Last == HIGH && btn1DnTime > long(debounce)){
    if (output1 == true) event1();
    if (output2 == true) event2();
    if (output3 == true) event3();
    if (output4 == true) event4();
    btn1UpTime = millis();
  }

// ################## OUTPUTs 1 - 4 for button 2 #################
  if (button2Val == LOW && button2Last == HIGH && btn2DnTime > long(debounce)){
    if (output1 == true) event5();
    if (output2 == true) event6();
    if (output3 == true) event7();
    if (output4 == true) event8();
    btn2UpTime = millis();
  }

}

// ****************************************** CODE FOR RELEASE MODE *************************************************************

if (ReleaseModeOn == true)
{
  
// ################## OUTPUTs 1 - 4 for button 1 #################
// Test for buttons release and store the up time

    if (button1Val == HIGH && button1Last == LOW && (millis() - btn1DnTime) > long(debounce))
      {
      if (ignore1Up == false && output1 == true) event1();
      else if (ignore1Up == false && output2 == true) event2();
      else if (ignore1Up == false && output3 == true) event3();
      else if (ignore1Up == false && output4 == true) event4();
      else ignore1Up = false;
      btn1UpTime = millis();
      }

// ################## OUTPUTs 1 - 4 for button 2 #################
    if (button2Val == HIGH && button2Last == LOW && (millis() - btn2DnTime) > long(debounce))
      {
      if (ignore2Up == false && output1 == true) event5();
      else if (ignore2Up == false && output2 == true) event6();
      else if (ignore2Up == false && output3 == true) event7();
      else if (ignore2Up == false && output4 == true) event8();
      else ignore2Up = false;
      btn2UpTime = millis();
      }

}

// ############ count btnDnTime ############### repeat the code for button one if want to change output mode with button 2
   if (button2Val == LOW  && (millis() - btn2DnTime) > long(holdTime))
      {
      ignore2Up = true;
      btn2DnTime = millis();
      }
      
// ##################################################### MODE CHANGE EVENTS ################################################


// CHANGE FROM OUTPUT 1 TO OUTPUT 2
        if (button1Val == LOW && (millis() - btn1DnTime) > long(holdTime) && output1 == true)
      {
      eventModeChange();
      ignore1Up = true;
      btn1DnTime = millis();  
      output1 = false; 
      output2 = true;
      output3 = false;
      output4 = false;
      }

 

// CHANGE FROM OUTPUT 2 TO OUTPUT 3
    if (button1Val == LOW && (millis() - btn1DnTime) > long(holdTime) && output2 == true)
      {
      eventModeChange();
      ignore1Up = true;
      btn1DnTime = millis();  
      output1 = false; 
      output2 = false;
      output3 = true;
      output4 = false;
      }

// CHANGE FROM OUTPUT 3 TO OUTPUT 4
    if (button1Val == LOW && (millis() - btn1DnTime) > long(holdTime) && output3 == true)
      {
      eventModeChange();
      ignore1Up = true;
      btn1DnTime = millis();  
      output1 = false; 
      output2 = false;
      output3 = false;
      output4 = true;
      }

// CHANGE FROM OUTPUT 4 TO OUTPUT 1
    if (button1Val == LOW && (millis() - btn1DnTime) > long(holdTime) && output4 == true)
      {
      eventModeChange();
      ignore1Up = true;
      btn1DnTime = millis();  
      output1 = true; 
      output2 = false;
      output3 = false;
      output4 = false;
      }
    
button1Last = button1Val;
button2Last = button2Val;

}

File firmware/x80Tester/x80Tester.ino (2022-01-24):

// Header Files
#include "X80Config.h"
#include "pitches.h"
#include <Adafruit_DotStar.h>
#include <EasyBuzzer.h>

// Variable declarations

// An alternative way of defining the switches

const int switchCount = 5;
uint8_t inputSwitches[switchCount] = { SWITCH_INPUT_ONE, SWITCH_INPUT_TWO, SWITCH_INPUT_THREE, SWITCH_INPUT_FOUR, SWITCH_INPUT_FIVE };

byte switchState[switchCount] = { LOW, LOW, LOW, LOW, LOW };

const int switchInterval = 100;    //number if milliseconds between switch readings. Also allows for debounce


int switch1State = 0;
int switch2State = 0;
int potValue = 0;
float battVoltage = 0;
int switchValue = 0;


//Dotstar LED definitions
// There is only one pixel on the board
#define NUMPIXELS 1 

//Use these pin definitions for the ItsyBitsy M4
#define DATAPIN    8
#define CLOCKPIN   6

Adafruit_DotStar strip(NUMPIXELS, DATAPIN, CLOCKPIN, DOTSTAR_BRG);

// Define colours for DotStar LED

uint32_t colour_ace_light_blue = strip.Color(106, 157, 199);
uint32_t colour_ace_dark_blue = strip.Color(0, 83, 127);
uint32_t colour_ace_green = strip.Color(171, 204, 89);
uint32_t colour_ace_orange = strip.Color(225, 136, 0);
uint32_t colour_red = strip.Color(255, 0, 0);
uint32_t colour_green = strip.Color(0, 255, 0);
uint32_t colour_blue = strip.Color(0, 0, 255);
uint32_t colour_orange = strip.Color(255, 165, 0);

// Ace Sound played on startup
int aceSound[] = { NOTE_AS6, NOTE_A6, NOTE_F5, NOTE_CS5, NOTE_D5, NOTE_F5, NOTE_AS4 }; // notes in the melody:
int aceSoundNoteDurations[] = { 8, 4, 4, 16, 4, 4, 4, 4 }; // note durations: 4 = quarter note, 8 = eighth note, etc.:

int buttonState = 0;


unsigned long currentMillis = 0;          // stores the value of millis() in each iteration of loop()
unsigned long previousButtonMillis = 0;   // time when button press last checked.

int sensorValue = 0;
int outputValue = 0;

void setup() {

  
  Serial.begin(9600);

  //playAceSound();

  //Set the Easy Buzzer Pin
  EasyBuzzer.setPin(BUZZER_PIN);

// Dotstar stuff
  strip.begin(); // Initialize pins for output
  strip.setBrightness(80);
  strip.show();  // Turn all LEDs off ASAP

  pinMode(LED_BUILTIN, OUTPUT);  // initialise built in LED
  digitalWrite(LED_BUILTIN, LOW);

  // Temporary setup of input switch
    // initialize the LED pin as an output:
    // initialize the pushbutton pin as an input:
  pinMode(SWITCH_INPUT_ONE, INPUT);     // Only this inout has it's own pull up resistor
  pinMode(SWITCH_INPUT_TWO, INPUT_PULLUP);
  pinMode(SWITCH_INPUT_THREE, INPUT_PULLUP);
  pinMode(SWITCH_INPUT_FOUR, INPUT_PULLUP);
  pinMode(SWITCH_INPUT_FIVE, INPUT_PULLUP);  // Ned to check this one's working with a splitter

  pinMode(SWITCH_OUTPUT_ONE, OUTPUT);  // initialise built in LED
  pinMode(SWITCH_OUTPUT_TWO, OUTPUT);  // initialise built in LED
  pinMode(SWITCH_OUTPUT_THREE, OUTPUT);  // MIGHT BE THIS LINE THAT'S CAUSING THE PROBLEM
  pinMode(SWITCH_OUTPUT_FOUR, OUTPUT);  // initialise built in LED   
        
  pinMode(RELAY_DRIVER, OUTPUT); 
  
  //digitalWrite(RELAY_DRIVER, HIGH);

  SWITCH_OUTPUT_ONE_OFF;
  SWITCH_OUTPUT_TWO_OFF;
  SWITCH_OUTPUT_THREE_OFF;
  SWITCH_OUTPUT_FOUR_OFF;

  SWITCH_ONE_PASSTHROUGH_DISCONNECT;


            //potValue = analogRead(POT_PIN);  // get potentiometer value
          //Serial.print("Pot Setting: ");
          //Serial.println(potValue);
   
}

void loop() {

  currentMillis = millis();

  readSwitches();
  actionOutputs();
  
  EasyBuzzer.update();

  outputValue = analogRead(POT_PIN);
  Serial.println(outputValue);

//String switchArray[switchCount] = { "A4", "A3", "A2", "A1", "A0" };

/*
  // read the state of the pushbutton value:
  buttonState = digitalRead(switchArray[1]);

  // check if the pushbutton is pressed. If it is, the buttonState is HIGH:
  if (buttonState == HIGH) {
    // turn LED on:
    digitalWrite(LED_BUILTIN, LOW);
  } else {
    // turn LED off:
    digitalWrite(LED_BUILTIN, HIGH);
  }
*/





  
}

void ledTurnOn(uint32_t colour) {

  //strip.show(); // Update strip with new contents
  strip.setPixelColor(0, strip.gamma32(colour));
  strip.show();
 
}

void ledTurnOff() {

  strip.setPixelColor(0, 0, 0, 0);
  strip.show(); // Update strip with new contents  
  
}


void audibleFeedback (int type) {

  switch (type) {
    case AUDIBLE_INFORMATION:
      tone(BUZZER_PIN, 925);
      break;
    case AUDIBLE_WARNING:
      tone(BUZZER_PIN, 500);
      break;
    default:
      tone(BUZZER_PIN, 500);
      break;
  }
}

void playAceSound () {

  // This is the Ace sound
  
  /*
  for (int thisNote = 0; thisNote < 8; thisNote++) {              // iterate over the notes of the melody:

    int noteDuration = 1000 / aceSoundNoteDurations[thisNote];    // calculate the note duration, e.g. quarter note = 1000 / 4
    tone(BUZZER_PIN, aceSound[thisNote], noteDuration);
    int pauseBetweenNotes = noteDuration * 1.13;                  // to distinguish the notes specify pause
    delay(pauseBetweenNotes);
    noTone(BUZZER_PIN);                                           // stop the tone playing:

  }
  */
  
}
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

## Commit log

2021-03-10 Folder structure updated for current versions
    [112-001-B_v1.0_BOM.xlsx, Feather_Ace_Shield.brd, Feather_Ace_Shield.sch, Modular Assistive Technology Interface.GBL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]
2021-08-08 Included Version 4
    [630-001 X80 Main Board Enclosure v39.f3d, X10 - Main Board_RevB.brd, X10 - Main Board_RevB.sch, X80 Enclosure Base.stl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]
2021-08-08 Added PCB schematic pdf
2022-01-24 Changes made to hardware enclosures and folder structure
    Removed references to previous versions. Changed file structure to make easier to follow. Added example code.
    [112-001-B_v1.0_BOM.xlsx, 630-001 X80 Main Board Enclosure v39.f3d, 630-002-A X80 Enclosure Base Basic.stl, 630-003-A X80 Enclosure Lid Basic.stl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]
2022-01-24 Lens and Mounting plate moved to parts folder
    [630-005-A X80 LED Lens.stl, 630-006-B X80 Mounting Plate.dxf, 630-006-B X80 Mounting Plate.stl]
2022-02-09 adding circuitPy demo
2022-02-10 Enclosure updated
    [630-014 X80 Enclosure Wio Terminal Base.stl, 630-014 X80 Enclosure Wio Terminal Lid.stl]
2022-06-14 Add v1 of circuit python
2023-01-25 Adding Wireless Switch demo.
    NB: This won't work on an X80 right now. This works on any nrf52840 chipset and note to add LED and Switches for the right pins.
2023-01-26 sleep functionality added
    If there is no switch presses for defined amount of time then the board goes into deep sleep.
    This amount of time can be adjusted with "sleep_timeout" variable at line 8.
    Default value is 5 seconds.
    To wake up boards it's needed to press the switch .
    First press will be for board wake up and after built in led will turn on board will be ready to transmit data.
    It takes about 1 second.
2023-01-28 Including battery details
2023-02-13 adding boards
2023-02-23 adding raw gerbers files
    [DD5018-B_Cu.gbr, DD5018-B_Mask.gbr, DD5018-B_Silkscreen.gbr, DD5018-Edge_Cuts.gbr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]

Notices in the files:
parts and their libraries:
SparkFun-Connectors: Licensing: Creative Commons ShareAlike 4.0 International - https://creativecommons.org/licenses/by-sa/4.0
